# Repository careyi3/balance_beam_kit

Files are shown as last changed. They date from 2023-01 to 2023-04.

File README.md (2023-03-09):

# Balance Beam Kit

Welcome to the source for all of the resources relating to the Ball & Beam kit! This is where we host all of the downloadable resources for the project including the documentation.

To get started with the project, please [head over to the docs site!](https://careyi3.github.io/balance_beam_kit/)

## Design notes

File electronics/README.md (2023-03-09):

# Electronics

Here are all the GERBER files required to produce the PCB for this project along with a BOM and CPL file required to assemble the boards with JLCPCB.

To learn more about the electronics for this project, [head to the electronics section of the docs!](https://careyi3.github.io/balance_beam_kit/electronics/)

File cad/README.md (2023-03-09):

# CAD

Supplied here are the `.stl` files needed to print your own versions of the required parts.

Also included here is my g-code for printing the parts on my Ender3 V2. These g-code files are included for my reference to keep track of my own work, these more than likely won't work for you, do not use them, please slice your own.

To learn more about the mechanical assembly for this project, [head to the assembly section of the docs!](https://careyi3.github.io/balance_beam_kit/assembly/)

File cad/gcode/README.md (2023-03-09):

# G-Code

* DO NOT USE *

This g-code was generated for my Ender3 V2 and has absolutely no guarantee of working for your printer. Please slice the `.stl` files provided under `../meshes`.

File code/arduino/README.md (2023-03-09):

# Code

Included here is test and sample code for the rig. Under `ball_and_beam` you will find the main Arduino sketch implementing a simple PID loop to stabilise the ball along the midpoint of the beam.

Along side the main code under `tests`, you will find simple test code for interfacing with the stepper via the driver and for interfacing with the acoustic position sensor.

To learn more about the code for this project, [head to the programming section of the docs!](https://careyi3.github.io/balance_beam_kit/programming/)

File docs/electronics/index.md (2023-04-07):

---
layout: page
title: Electronics
permalink: /electronics/
---

In this section we are going to break down our discussion into four main topics for discussion; stepper motors and drivers, the Arduino microcontroller, the ultrasonic position sensor and finally the PCB. Before we talk about the PCB I have also included a basic diagram of a breadboard version of the circuit and some tips on assembly etc. The most advanced topic of the discussion is the PCB and in this section we will also discuss the details of the design of the power switching circuit on the board. The final section is optional and fairly abstract, but if you want to dive into some analog electronics design, it's worth a read.

&nbsp;

---

&nbsp;

## Arduino

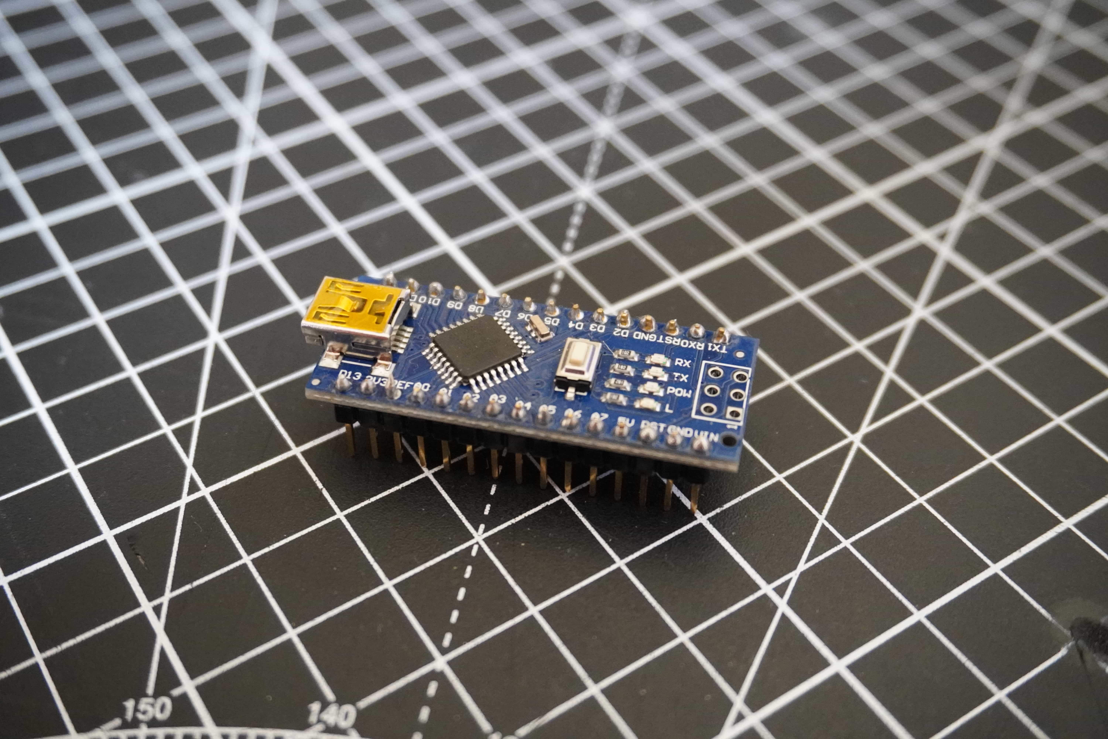
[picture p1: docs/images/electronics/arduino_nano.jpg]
arduino nano


An Arduino is a low cost, flexible, simple and robust microcontroller development platform originally built around Atmel microcontrollers. In the wild, microcontrollers are the smart chips that control electronic devices. Microcontrollers are tiny programmable computers that exist on a single chip. In terms of electronics, they occupy the space somewhere between things that are simple on-off devices with analog components and fully fledged computers. That is to say, a microcontroller can typically interface with simple low level electronics but can bring some intelligence to them while not having the power of a full computer. Even tho these devices don't have the computing power of full computers, modern microcontroller are incredibly powerful and capable of doing amazing things. Microcontroller shine in their ability to do relatively complex tasks at a low level very fast while consuming very little power. Consider that a modern computer has to be able to do lots of different things all at once, typically a microcontroller only has to do one or a small hand full of things at a time; in this way, they can be highly optimised for the task at hand.

While there are loads of different kind of microcontroller available these days, Arduino's provide a great platform to learn embedded software development and electronics. It should be noted that "an Arduino" is a development board and accompanying software stack for developing embedded software projects and not specifically a microcontroller. The microcontroller is the little chip on the board that is the brains of the operation. However, Arduino's are usually referred to as microcontrollers, all be it slightly incorrectly. Arduino's are cheap and very robust, they are hard to blow up compared to other kinds of microcontroller, and when they are blown up, they are easily replaceable. Arduino's also come with a companion software development environment and a whole host of nice libraries and hardware abstractions which means you can get up and running really quickly. There is also a huge online community ready and willing to provide support.

For all of the above reasons and more, I choose to base the kit around an Arduino. I also have a lot of experience personally working with these devices so it was quick for me to prototype the system using one.

To learn more about Arduino I suggest visiting their [website](https://www.arduino.cc/) where you can find loads of information on them. Aside from the basic background presented here, we will dive into more detail about working with an Arduino in the [programming](../programming) section of this guide.

For this project, we will use an Arduino Nano. You can use any Arduino for this, but if you wish to use the PCB for the project, it has a socket which will accept an Arduino Nano. Also note, if you are sourcing an Arduino for the first time, you can buy them from the Arduino website, however these days you can buy many many clones of them online. They are all largely the same, some might have slight differences. Largely these are fine to use but buy them at your own risk as some can be faulty. With that said, they are usually available at a fraction of the price of the branded versions.

&nbsp;

---

&nbsp;

## Stepper Motors & Drivers

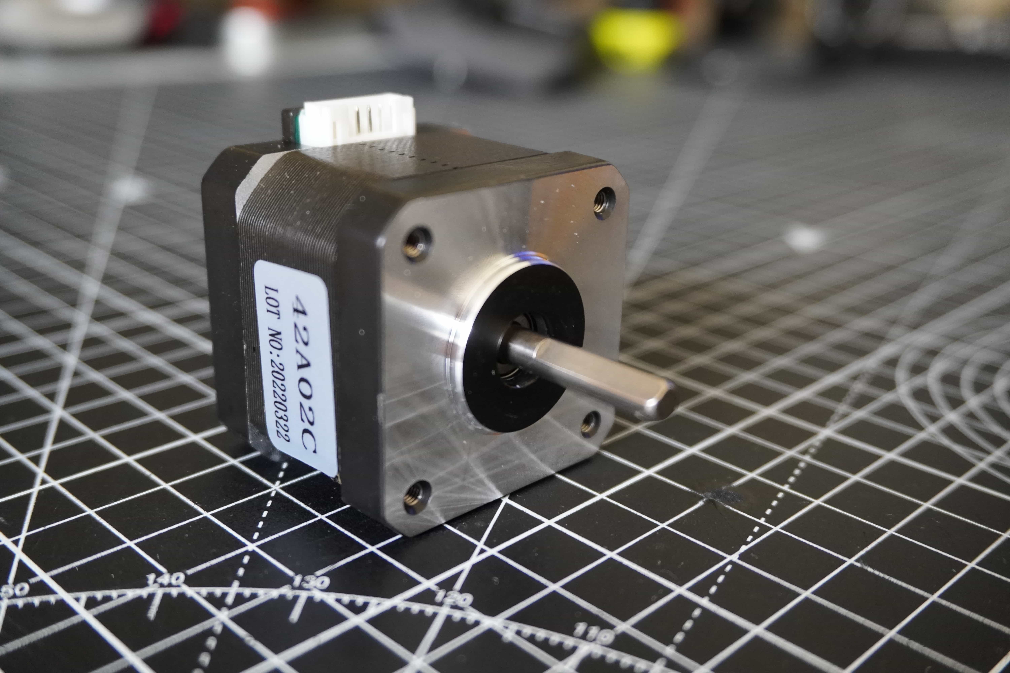
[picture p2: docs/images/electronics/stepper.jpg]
stepper


Stepper motors are a special kind of brushless DC motor that are capable of accurate positioning with no external sensors under normal operation. This means that you can command the motor to spin a certain amount of degrees and hold it's position. The motor will move to the commanded position and stay there with very little error. This effect is achieved pulsing coils in the motor in a certain pattern, the magnetic field created with these coils then interacts with a specially shaped toothed rotor in the motor snapping the motor between so called "steps".

In this way, each rotation of the motor is actually made up of lots of small "steps" hence the motors name. In effect stepper motors are sort of like a poorly designed DC motor in that each state the motor gets into it doesn't really want to leave. This also means that at each step the motor has a very powerful holding torque and doesn't want to slip. These traits can be leveraged in many applications to make stepper motors extremely useful.

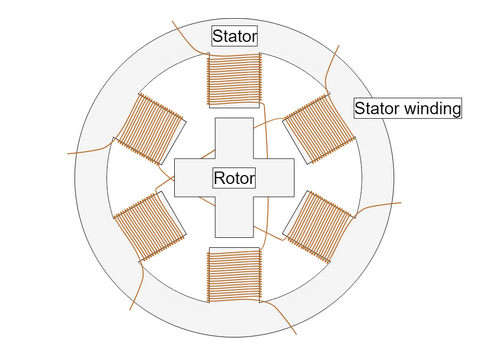
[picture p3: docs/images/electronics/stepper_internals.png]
stepper internals


In terms of machine control, you can work out how many steps correspond to a certain about of movement of an axis of a machine. Once this is known, you can tell the machine how far to move the axis byt sending the correct number of steps to the motor. Due to the way the motors moves in steps and doesn't want to slip from it's holding position, this is extremely accurate and does not require sensors to detect the actual position.

One common modern usage of stepper motors is in low cost desktop 3D printers. The prevalence of these devices has made the NEMA 17 form factor of stepper motor widely mass produced and easily purchased the world over for very low cost. However, they do come with certain disadvantages including extra complicity in their operation. Compared to a regular DC motor, stepper motors require a driver and controller to function. Typically you would use a stepper driver board to interface directly with the motor and a microcontroller to tell the driver when to step the motor. Thanks to the 3D printer market, stepper drivers are also widely available and cheap such as the DRV8825 and in general microcontrollers are also cheap these days, so the expense might not be huge but there is a step up in complicity with compared to flicking a switch for a DC motor.

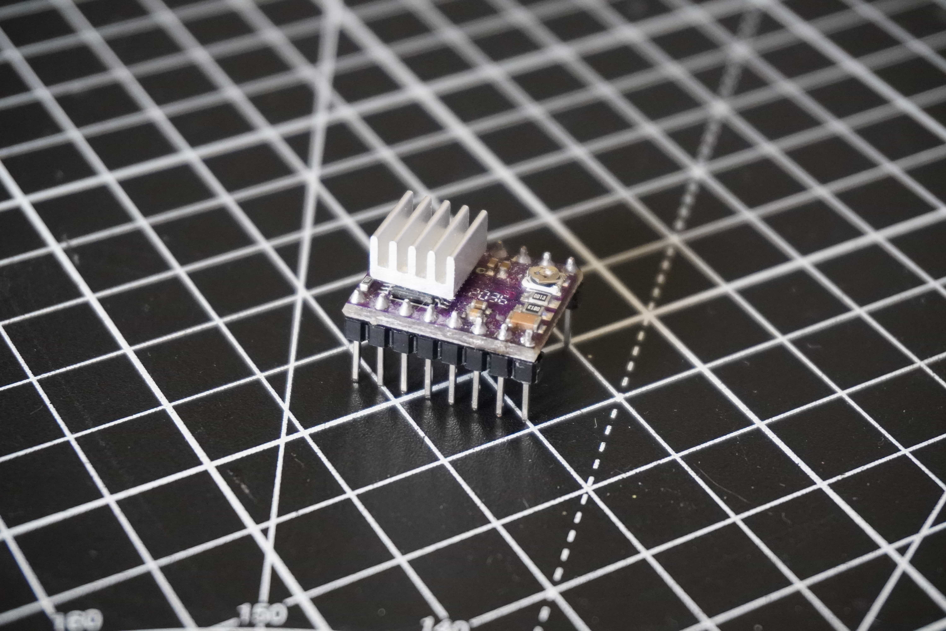
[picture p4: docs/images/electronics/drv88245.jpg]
DRV8825


Considering all of the pros above, a stepper is a decent choice for this project. However it may not be the best choice for all control type projects. The nature of this machine means that the motor doesn't need to move very fast. While moving fast is something stepper motors can do, there are limitations to how fast an Arduino can drive a stepper and so if you require very high speeds this might not be the best solution.

Without going into hugh detail, it's worth knowing that the maximum speed your stepper can attain with be related to how fast your driver can send pulses to the motor (along with how fast your motor can respond to the pulses). The driver in theory will send a pulse to the motor every time it receives a pulse from the microcontroller. Typically the driver will have a "step" pin, by pulsing it high and low from the microcontroller, it will then send a "step" pulse to the motor. There is a minimum pulse width required by the driver and also a theoretical max frequency of the pulses set by the clock speed of your microcontroller. For an Arduino using the widely used [AccelStepper library](https://www.airspayce.com/mikem/arduino/AccelStepper/) this more or less ends up maxing out the pulses per second to 4000 on an Arduino with a 16Mhz clock.

&nbsp;

---

&nbsp;

## Ultrasonic Position Sensors

In our system the "feedback" loop is created by the use of a HC-SR04 ultrasonic position sensor. This is a low cost high performance method of detecting objects by bouncing high frequency sound waves off them and measuring the time of flight of the pulses as they echo back to the module.

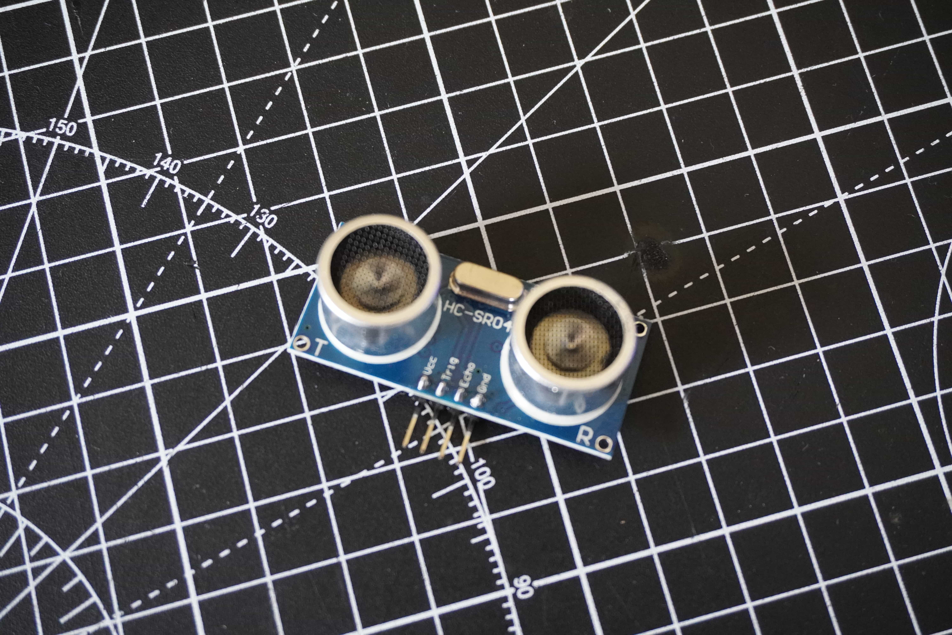
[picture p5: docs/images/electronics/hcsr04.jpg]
hcsr04


If you look at the modules you will see that there are two pieces that look like little speakers. In reality one if a speaker and one is a microphone. When the device is triggered, the speaker side emits pulses of sound which are then reflected back and picked up by the microphone side. The device generates output pulses which can then be measured by a microcontroller to determine the distance of the object reflecting the sound back to the sensor. Below is a graph of what the signals look like as they are transmitted.

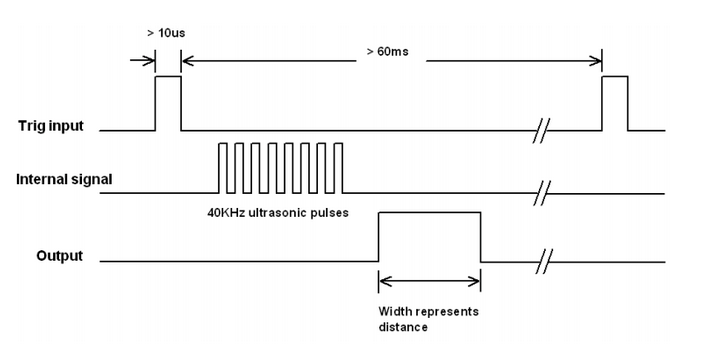
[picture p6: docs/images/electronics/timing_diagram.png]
timing diagram


These modules are fairly accurate however they have some limitations. Due to the nature of their signal, they work best when help perpendicular to a flat smooth surface. They also don't like turbulent air or high frequency vibrations in their vicinity. The only real limitation for our use case is that they also have a small deadzone as you get close to them, but this is handled by the design of the beam which has a built in buffer between the ball and the face of the sensor.

&nbsp;

---

&nbsp;

## Breadboard/Protoboard Circuit

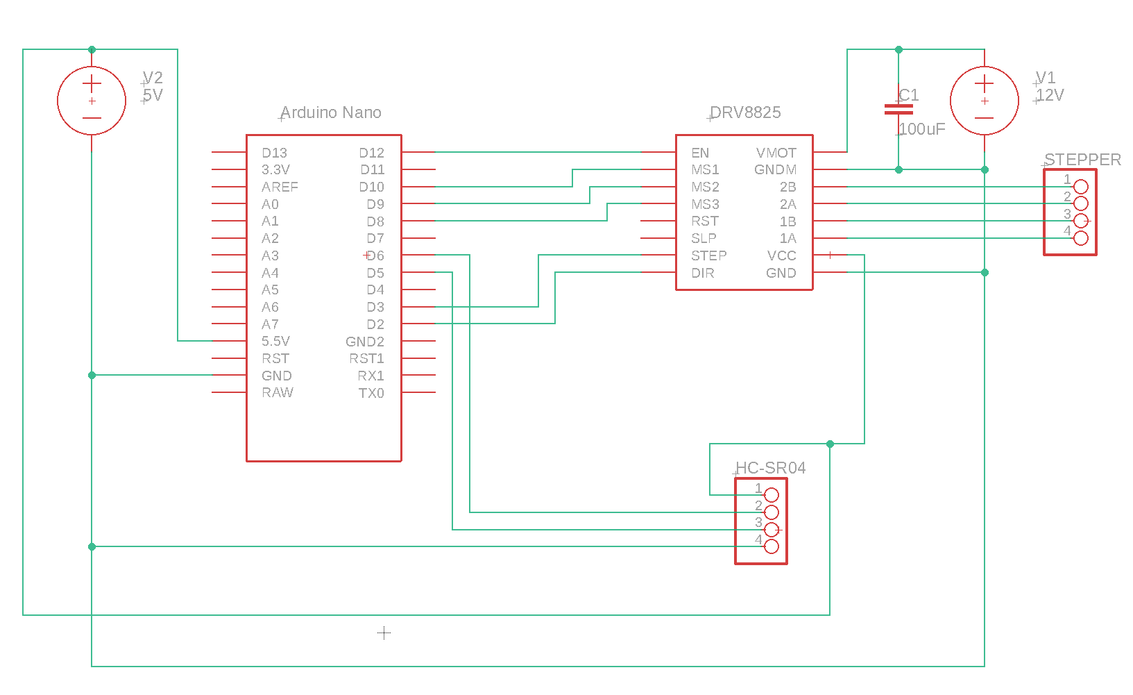
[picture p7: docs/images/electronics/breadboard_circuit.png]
breadboard circuit


The circuit above is fairly simple but there are a few nuances to take into account. Firstly, I would suggest powering the entire thing from a single power supply. I recommend a 12V 2A DC Walworth power supply. This will provide enough current for the motor and also can be stepped down using a voltage divider or a regulator to give 5V for the other electronic. Either this or you can use a USB cable to power the Arduino which will provide the 5V needed for the rest of the circuit. I like to use a single power supply so that I am sure I have the same ground everywhere.

There is a single 100uF capacitor connected to the motor supply line. This is simple an anti ripple capacitor. It is common for cheap power supplies to have some rippled in them, this helps to get rid of this which prevents noise from impacting the driver. This is an important component and it should not be left out.

&nbsp;

---

&nbsp;

## PCB

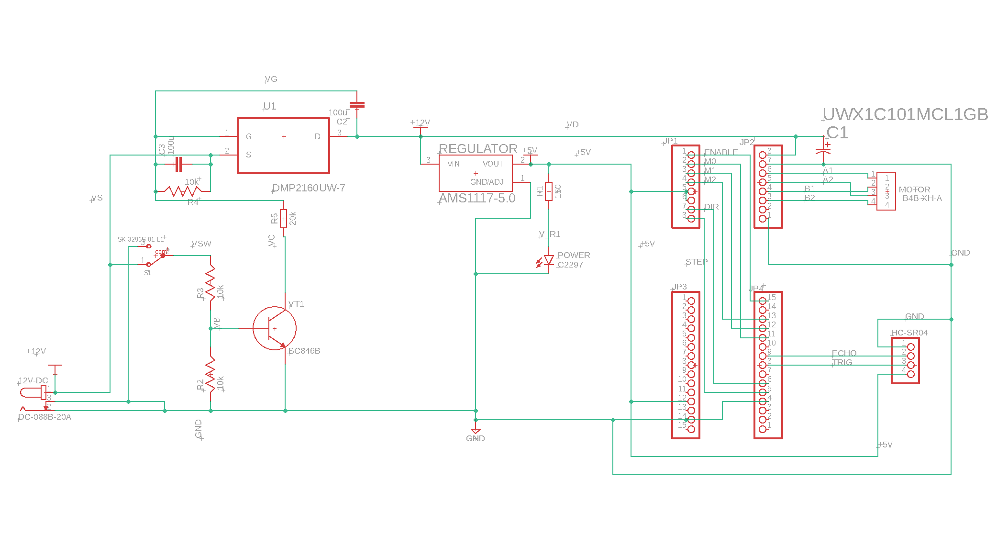
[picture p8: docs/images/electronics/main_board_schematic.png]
circuit diagram


For this project I designed a PCB because it was something I hadn't done before and wanted to try it out. With the consideration that this might one day be part of a kit, it also made sense to do this. If you are building your own version of this, the PCB isn't necessary unless, like me, you want to go through the process of getting one manufactured. That said, the design process is the more valuable part of getting your own made.

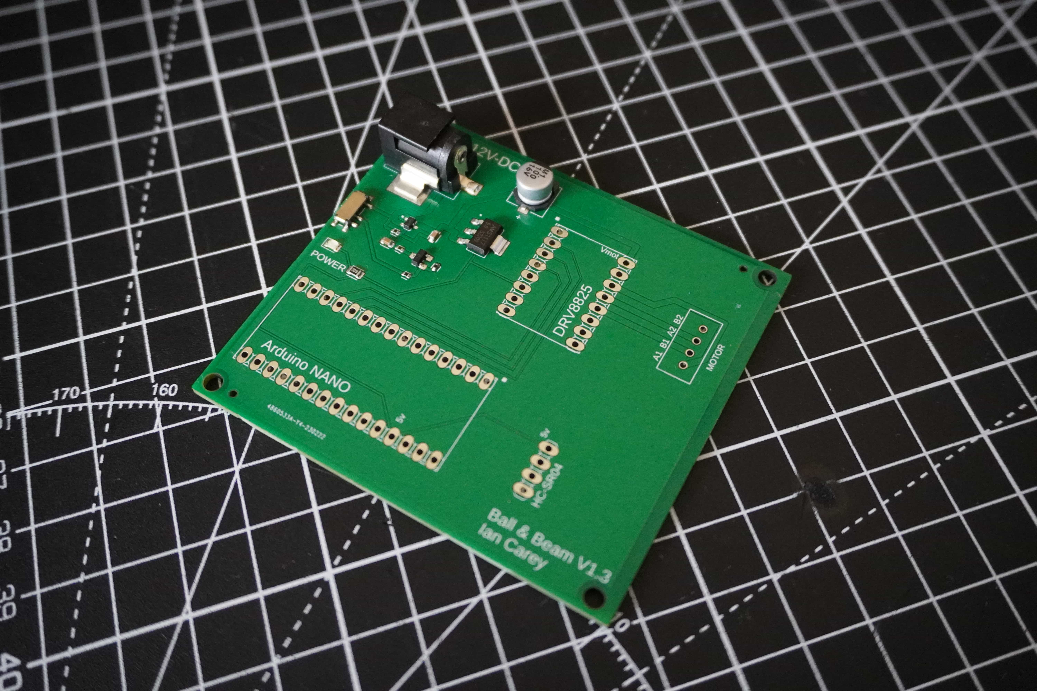
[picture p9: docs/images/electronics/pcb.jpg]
pcb


I'm not really an expert in PCB design and it's not critical for the project, so I am not going to go into much detail here. However, if you want to get your own made, you can find all the GERBER files [here](https://github.com/careyi3/balance_beam_kit/tree/master/electronics/manufacture) along with the bill of materials which will be accepted by the manufacturer I used [JLCPCB](https://jlcpcb.com/).

The PCB is really simple, it's mostly just plumbing together parts to make them nice and neat on one board. The traces are mostly just to connect the Arduino to the DRV8825 and to provide a port to plug the motor and sensor into. The most interesting bit of electronics on the board is actually the power supply that I designed with some help. I will go into this in more detail in the next section. It is however a more complex topic and totally unnecessary for the project. Feel free to skip over the next section unless you are specifically interested.

&nbsp;

---

&nbsp;

### Power Circuit

When I decided to design the PCB for this system, I knew I was getting myself in for lots of things I didn't know and lots of things I had log forgotten from studying engineering years ago. One thing I knew is that the power switch wasn't going to be simple. This might seem strange, but switching can be a tricky thing to do, especially on a PCB with components of varying power consumption. In our case, we have a power switch which needs to cut off power to a microcontroller and a sensor module, no big deal, these devices draw very little current, any tiny pcb mounted slide switch could handle it. However, we also need to cut off power to the motor driver and driver board, this is where the tricky part is. If you think about a basic switch, it's normal closed state is a broken circuit where the supply is on one side and the load on the other, no current flows, all good. When the switch is flicked, suddenly the supply and the load are connected, depending on the load, this could end up drawing a lot of current. Now, in our case the max current we could expect is in or around 1.5A max, that's not a huge amount of current in general, but, when you think that all of it will be being pull through a tiny little switch, you can probably guess the issues that might arise. In fact, if you look at the specs for most of the tiny slide switches on the market, they are all only rated for tiny current. Pulling anything close to 1A through them would surely burn them out immediately.

With all of this in mind, we need to come up with a solution to be able to switch a relatively heavy load on and off, with out the switch itself physically carry any of the load current. There are many ways to do this including the age old and simple mechanical relay. However, a more modern solution to the problem would be to use a switching circuit made up of transistors. Transistors are effectively electronic switches which can be turn on or off by changing certain conditions around them. Typically the physical components have three pins and by wiring them in a certain way, you can make them only conduct across their input and output when a certain voltage is provided to another one of their pins. Now, that is a very basic explantation, their are different flavours of these transistors and the ways in which they work is more complex than I described above, but that's the basics of what you should know about them. In our switching circuit we use two transistors to make our switch work. The full circuit diagram I used to design and simulate this is below. We won't worry about all of the circuit as some of it is just set up to simulate things, but I have highlighted the important parts.

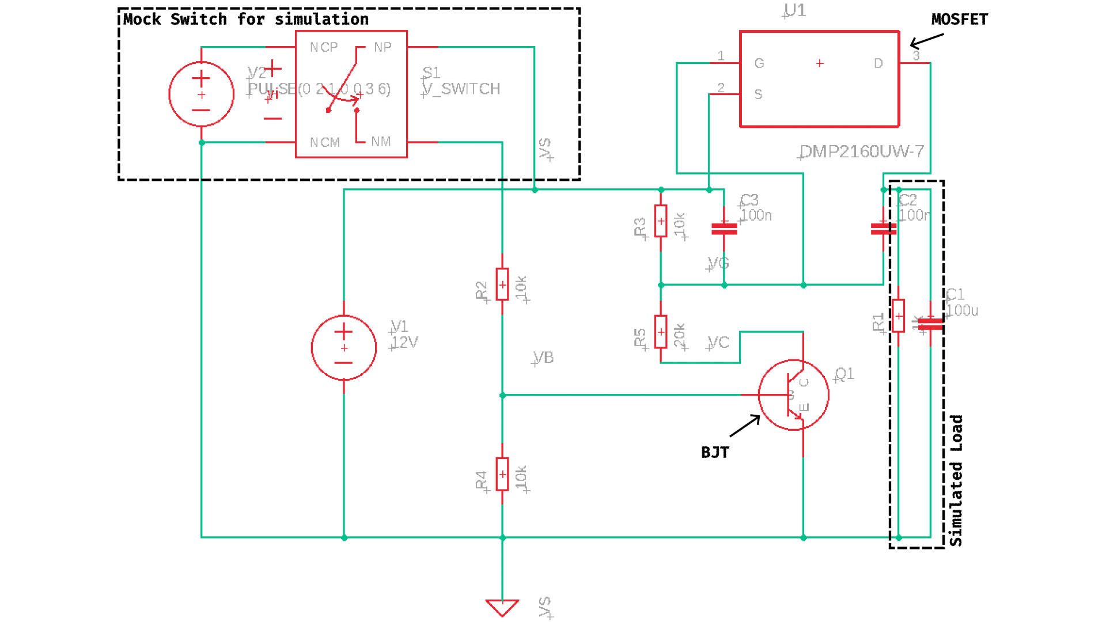
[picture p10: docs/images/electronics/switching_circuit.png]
switching circuit


In our circuit we are using two transistors which have slightly different characteristics. I won't get into the details of their differences but the two types are a Bi-Polar Junction Transistor (BJT) and a Metal-Oxide-Semiconductor Field-Effect Transistor (MOSFET). In terms of naming, I will just say that the pins on a BJT are named the collector, base and emitter. While on a MOSFET they are called the source, gate and drain. You can sort of think of the base and gate pins as being the on/off pins with the other two being the input and output. These components are highlighted in the above diagram. Also highlighted above are the two parts which are just for the simulation. These include an imaginary RC load and a switching circuit which allows for the "switch" to be flicked on and off in the simulation to see the different states over time. In your head, you can replace this with a normal switch being turned on and off by hand. Let get into how the circuit works.

In the initial state, the switch is turned off. With the switch off, the base of the BJT is pulled to ground via the resistor R4, this in effect turns off the BJT and no current flows between the collector and emitter. If we now look at the MOSFET, we see that it's gate pin is connected to a voltage divider in line with the collector of the BJT. With the BJT turned off, the lower branch of the voltage divider is ignored and with no current actually flowing through the gate of the MOSFET (that's just how they work), the voltage at the gate is effectively 12V i.e. it matches the supply voltage. You will notice that the source pin is also connected to the same 12V and so their is no voltage different between them. This is important, because the MOSFET will only turn on when the voltage difference between the source and gate exceeds a certain amount. Now, lets talk about the case when the switch is turned on. With the switch turned on, the BJT now has it's base connected to some proportion of the supply voltage. In this specific set up the BJT will enter "saturation" and will conduct between the collector and the emitter. Now if we go back to the voltage divider connected to our gate, the end of the divider at R5 is now effectively connected to ground meaning that the voltage divider now acts as normal and the voltage at the gate of the MOSFET will be 8V thanks to the 1:2 ration of the resistors R3:R5. We now have a case where our gate is at 8V and our source is at 12V. Now, the threshold of voltage difference has been exceeded and the MOSFET will turn on and conduct between source and drain. In our case, the output of the drain powers everything on our board.

The above is dense and I have glossed over many parts but I hope it makes some sense as to how we can switch a high load circuit without the switch it's self actually carrying any of the current. The only component in this circuit that really carries any current is the MOSFET. It just so happens that MOSFETS are designed very well for this task. The relatively high resistor values in the rest of the circuit are specifically to limit current flow in the switching circuit. The BJT is also not dealing with any high current either. As a final note, I haven't spoken about the two capacitors on the source and drain of the MOSFET. These are called charging capacitors and help lower the current spikes when the switch is turned on. If you have a load with lots of capacitors on it, when you turn on the power, all of the capacitors will effectively charge up all at once. This can cause a massive spike is current draw on switching and can lead to components blowing as they aren't rated to handle this. These charging capacitors help to smooth out the sudden current draw caused when switching a capacitive load.

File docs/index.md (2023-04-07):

---
# Feel free to add content and custom Front Matter to this file.
# To modify the layout, see https://jekyllrb.com/docs/themes/#overriding-theme-defaults

title: Welcome!
layout: home
---

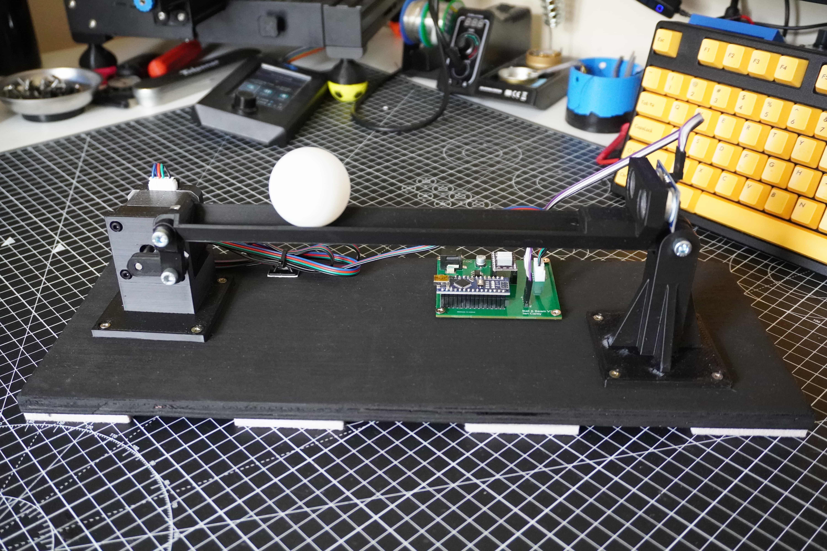
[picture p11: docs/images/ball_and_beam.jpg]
ball and beam


This is main project site for the Ball & Beam kit by Ian Carey. This guide covers everything you need to know to get up and running with the Ball & Beam kit from assembly, to programming to the theory behind how it works! The below sections are laid out so that they build on each other but you should jump in and out of them in what ever order makes the most sense to you.

All of the source materials, code, 3D printing files can be found here on the projects [Github repo](https://github.com/careyi3/balance_beam_kit). Enjoy!

The development of this kit has been fully documented on the creators YouTube channel, if you are interested, you can find the entire build series [here](https://www.youtube.com/playlist?list=PLMqshdJjWZdnB4wa5L2HWYxcJ6pagYxFq).

&nbsp;

---

&nbsp;

## Bill of Materials (BOM)

This is a list of all the materials you will need for this project. This project is currently still a fully DIY kit where we are only supplying the guide but you must supply all the parts. In future we hope to release purchasable kits that will contain the parts. For now, this is the best we can do.

[BOM](./bom)

&nbsp;

---

&nbsp;

## Assembly

Instructions, with photos, of the mechanical assembly of the rig. The assembly is straight forward enough involving only 5 3D printed parts all of which should easily be printable on most common 3D printers. For reference, all of the parts for this were designed to be printed on an Ender 3 V2.

[Assembly](./assembly)

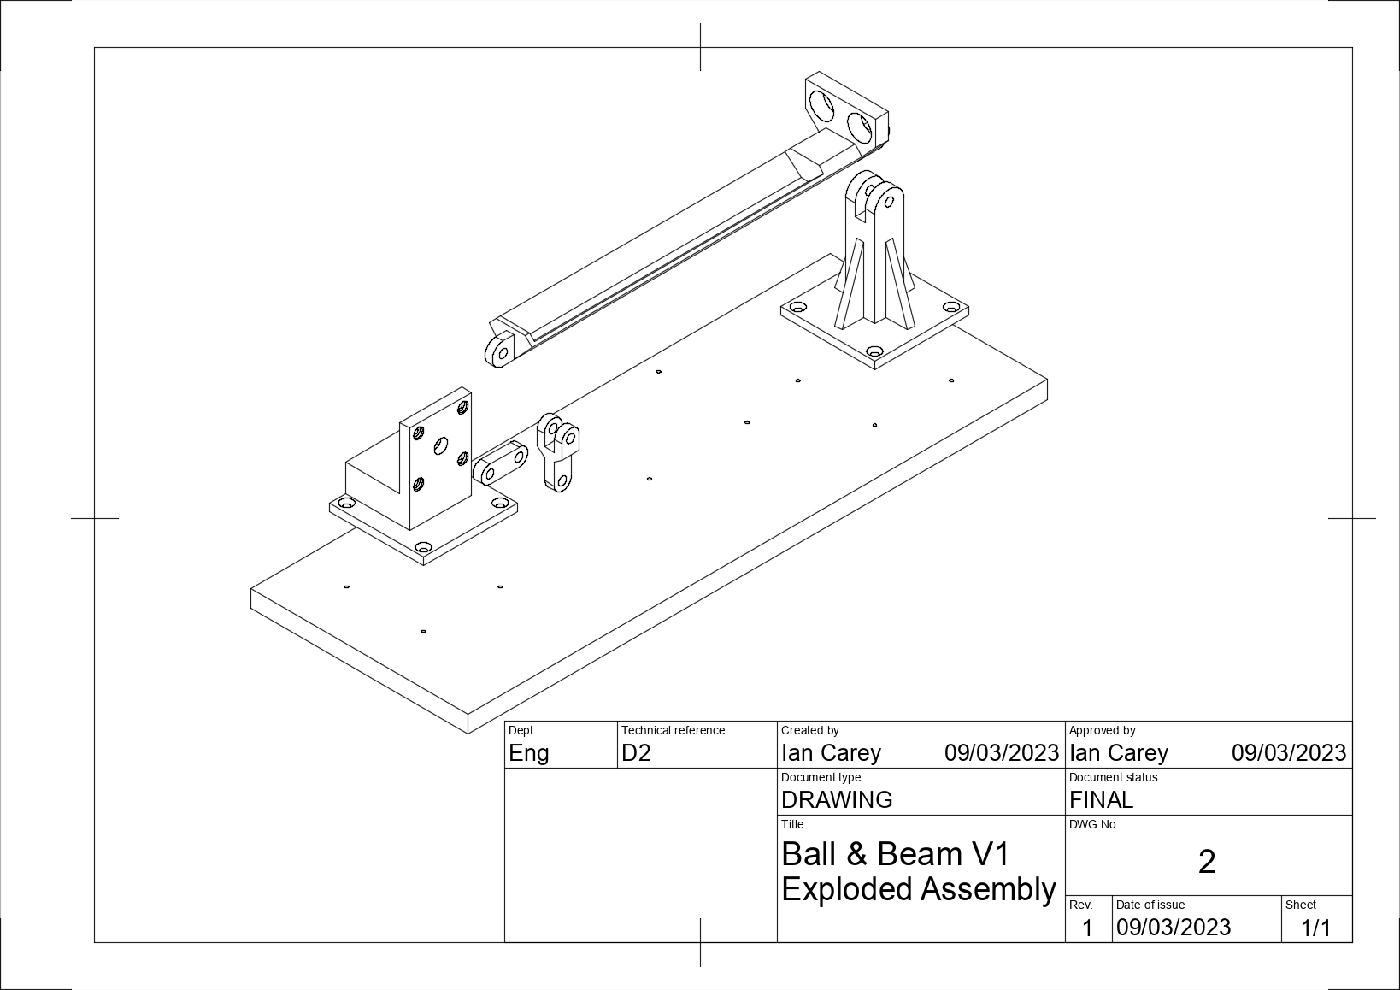
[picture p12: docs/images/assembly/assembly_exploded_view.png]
assembly_exploded_view


&nbsp;

---

&nbsp;

## Electronics

Details all of the the electronics involved, Arduino, stepper motors, position sensors and details of the PCB design.

[Electronics](./electronics)

main board schematic

&nbsp;

---

&nbsp;

## Programming

Details of the code involved in the system and working with the Arduino platform. We will also dig into the various libraries used in the project and how they work.

[Programming](./programming)

&nbsp;

---

&nbsp;

## Control Theory

In this section we will do an overview of the concepts behind control theory. The goal is to use as little maths as possible to give good overview of how a PID controller works and how it applies to our problem.

[Control Theory](./control_theory)

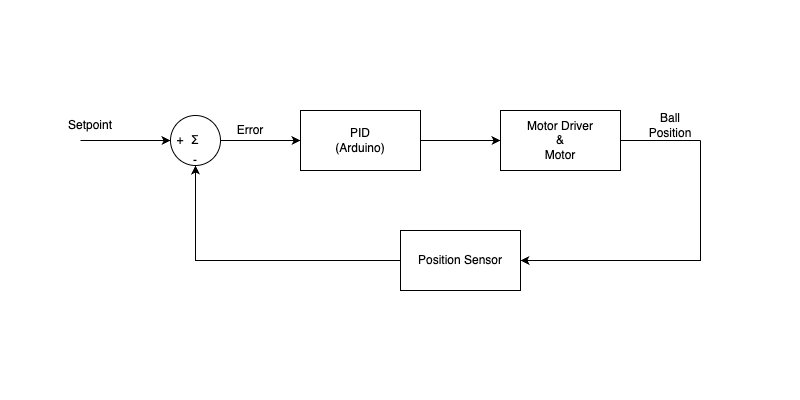
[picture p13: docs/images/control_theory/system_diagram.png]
system diagram


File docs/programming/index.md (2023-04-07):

---
layout: page
title: Programming
permalink: /programming/
---

In this section we will provide a basic overview of getting started with programming an Arduino microcontroller. We will then jump into some more complex discussion of how some of the important parts of the code work under the hood.

The sample code provided for the system is [here](https://github.com/careyi3/balance_beam_kit/blob/master/code/arduino/ball_and_beam/ball_and_beam.ino).

I have a [video on YouTube](https://www.youtube.com/watch?v=OBsXWNbOTRY) breaking down the code and going over it in some detail, it is a good companion to this guide if you want to take a look.

&nbsp;

---

&nbsp;

## The Basics

The Arduino platform is an extremely powerful and easy to use platform for getting up and running with embedded software development projects and requires very little prior knowledge to get started. The basic flow of how the system work goes like this; your microcontroller (usually an Atmel chip for Arduino) is soldered onto the Arduino board, you connect your Arduino board to your computer via USB. Using Arduino's software tools, you write your code in C/C++. Once written, the Arduino software interfaces with the microcontroller on the board and uploads your code to it. Once powered up, the microcontroller on the Arduino board then executes your code continuously. This flow is a little different to how production grade chips would usually work. Typically, microcontrollers require a special programmer to program or flash them with the required machine code. With Arduino, this is avoided by the microcontroller coming with a "bootloader" pre installed. This bootloader allows a very high level software interface to program the chip over USB.

I am not going to go into the details of setting up your first project with an Arduino, there are countless resources online for this the best of which is the basic Arduino getting started guide. If this is your first time working with this platform I highly recommend you take a look and follow the [getting started guide](https://docs.arduino.cc/learn/starting-guide/getting-started-arduino).

The rest of this section is going to go into the details and usage of specific libraries used in the example code for the system. It assumes that you have the code downloaded and can follow along with it. You can grab the code [here](https://github.com/careyi3/balance_beam_kit/blob/master/code/arduino/ball_and_beam/ball_and_beam.ino).

&nbsp;

---

&nbsp;

## AccelStepper Library

Stepper motors, as we covered in the electronics section, require more than just a simple on/off switch to control. Along with the stepper driver board, you need to write some code on your microcontroller to tell the motor driver when to send pulses. At it's most basic, you can interface with a stepper driver by pulsing a pin high and low (high for a minimum duration of 10us usually) at a particular frequency. On an Arduino, you can do this using `digitalWrite` and `delay`. This isn't the most advanced way of doing it, but it will work. Of course, the speed them of the motor is effectively controlled by the frequency of the pulses. So sending a step high low pulse with a shorter `delay` value between each pulse, you can make the motor spin faster.

While the above mechanism for pulsing a motor will work file for lots of different cases, it lacks some features that are very important for controlling a motor. One major thing missing from the above is acceleration. When working with electric motors in general you will find that one way they are specced is with torque-speed curves. These are plots of the amount of torque they have a certain speeds. A rough way to think about this is that the motor will have less torque at higher speed. So if you had a machine, like a cnc machine with a large enough mass, you can't just tell the motors to go full speed from a dead stop. The motors will stall immediately the not be able to move the machine. Instead you can start the motors spinning at a slower rate and ramp the speed up to full speed. A ramp down can then be used to slow the machine down to stop precisely at the desired location. These so called acceleration profiles are a bit more complicated to implement so it might be nice to use a library that implements this for us.

For this project I used the [AccelStepper](http://www.airspayce.com/mikem/arduino/AccelStepper/) library which handles basic operations of a motor as well as implementing accelerations and different operating modes like running a motor at a specific speed or moving it a specific number of steps at a certain speed. Thanks to stepper motors precise open loop position control, the software can also provide accurate tracking information on the exact angle of the stepper motor, including how many revolutions it's moved through and in which direction. I have used this library in many projects and I can honestly say I think it's fantastic. I strongly recommend having a read of the documentation and getting to grips with how it works, it is highly worth while. It has lots of config that is worth understanding including the limits to the maximum speeds and accelerations.

&nbsp;

---

&nbsp;

## HC-SR04 Library

With reference to the electronics section where we presented the timing diagram for this device, we should remember that the width of the pulse returned by the device should be measured to determine the distance from the sensor and object is. To trigger the device, all we have to do is send a pulse of a certain length to the device on the trigger pin. We then need to "listen" for a response on the echo pin and record the length of it. This might sound complicated but we can achieve the trigger pulse by using `analogWrite` and `delay` and we can listen to and record the response pulse length using the `pulseln` function. There is then a tiny bit of maths that needs to be done involving the speed of sound to turn the pulse length into a distance. None of this is very difficult bu there is a nice library we are using here which wraps all of this up in a handy package. You can find the source code [here](https://github.com/gamegine/HCSR04-ultrasonic-sensor-lib/). I recommend having a read of it and understanding what is going on.

&nbsp;

---

&nbsp;

## Kalman Filter

The above sensor library and the sensor module are pretty good at what they do especially considering the price of the modules. They have their limitations but within their operating ranges they work pretty well and should achieve enough accuracy for most hobby applications. The range of the sensors is from about 2-400cm, so if you are detecting objects at around a meter or so away and you don't need to worry about variances of 1-2cm, these sensors will work perfectly as they are. In our application, we are using the sensor in about the 2-30cm range and within that range a 1-2cm variance is going to be way to much error for the PID controller to stabilise it properly. Now, in real life, over the 2-30cm range the sensor isn't giving 1-2cm of variance, but there is still some noise in the sensor readings making them a little harder to use in the PID controller. As the PID controller changes it's input based on the error signal from the sensor, if this error signal has lots of noise, the PID controller has to compensate for this making it difficult to reach stability.

We can improve the situation a lot by using something to smooth out the noise in our sensor readings. There are many different ways to achieve this but by far one of the most effective ways is to use a Kalman filter. I am not going to go into the details of a Kalman filter here as they are a relatively complex and deep topic. For an amazing coverage of them, I highly recommend following [this tutorial on YouTube](https://www.youtube.com/playlist?list=PLX2gX-ftPVXU3oUFNATxGXY90AULiqnWT), watching the first 4-5 videos in the series will give you a really good working knowledge of the basic version used in our project here (I have always struggled with these and this videos series really cleared up lots for me). At a very high level view, the Kalman filter uses predictions of errors compared with actual measurements of values to build a model of the system under the hood. Amazingly, this model very quickly approaches an extremely accurate output of the real values of the system even if there is lots of noise present.

Regardless of if we understand the details or not, we can ignore the implementation if we use one of the great Kalman filter libraries available to us! For this project we use the excellent [SimpleKalmanFilter](https://github.com/denyssene/SimpleKalmanFilter) library as it works well for a single variable and doesn't over complicate the system. I suggest reading their docs about setting up the library but really we are only required to pass in some tuning parameters to initalise the state of the filter. These can also be tuned with trial and error to get it working the way you want.

&nbsp;

---

&nbsp;

## Coding a PID Controller

The main logic of the code for the system essentially follows a pattern of; read sensor -> process data -> command motors. This continues in a loop forever attempting to balance the ball at a set point. The part in the middle, "process data", is where the magic really happens in converting the sensor data into the correct motor commands to make the machine do what it needs to do. In specific it does this by implementing a PID controller. In the next section of this guide I will dive into control theory and the basic intuition around how a PID controller works and what it is doing. In terms of the software, we are using a library in the example code, but coding your own PID controller isn't very hard once you understand the concept. If you already know a bit about this subject but haven't seen how to do it from scratch I recommend you take a look at this [YouTube video](https://youtu.be/RZW1PsfgVEI) that walks through a basic from scratch implementation of a PID controller on an Arduino. If you don't know anything about PID controllers I recommend going to the [control theory](./control_theory) section and reading up and coming back to this video later.

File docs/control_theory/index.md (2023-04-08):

---
layout: page
title: Control Theory
permalink: /control_theory/
---

The main goal of the project is to act as a resource for teaching the basics of control theory and in particular the practical implementation of a PID controller. Below is a system diagram showing the main components of the system and their connection in the common system diagram format.

system diagram

Before we dive into the details, there are two videos of mine which will help, this first one is dedicated to explaining the [software behind the system in general](https://www.youtube.com/watch?v=OBsXWNbOTRY) and the next one is an in depth look at [implementing your own PID controller from scratch on an Arduino](https://youtu.be/RZW1PsfgVEI) (you may want to wait until after you have read this to watch, or not, who knows!).

## What is a System?

In engineering there came a point where machines started to evolve from being purely mechanical. With the advent of electricity and electric motors, there became a need to use a common framework to control system containing both electrical and mechanical elements. However, before we could control such a system, we need a common way of modelling it. To this end, the idea of systems & control theory started to come about. There are lots of formal maths that surround this topic, however we are only going to lightly touch on that here.

Typically we can thing of a system as being anything either electrical or mechanical or both, that takes some input that we can model and produces some output that we can also model. Usually the model of a system would be some mathematical function where we write the output as a function of the input. With expressions for the input and output we can define something called the transfer function for the system. This is basically a single mathematical expression that defines the characteristic of the system we are working with. Again, not getting into the details but this function is labelled `G(s)` and is the Leplace transform of the input expression divided by the Leplace transform of the output expression. If you feel comfortable looking into the maths behind this, I suggest researching the topic on your own. I can highly recommend Modern Control System by Dorf & Bishop for this topic.

For this discussion I only want you to be aware that a highly complex system can be broken down into a single function that defines it's behaviours and in control engineer we would refer to it via it's transfer function. In terms of control theory, we often refer to the system being controlled as the "plant". We would also often present it in block diagram for like below.

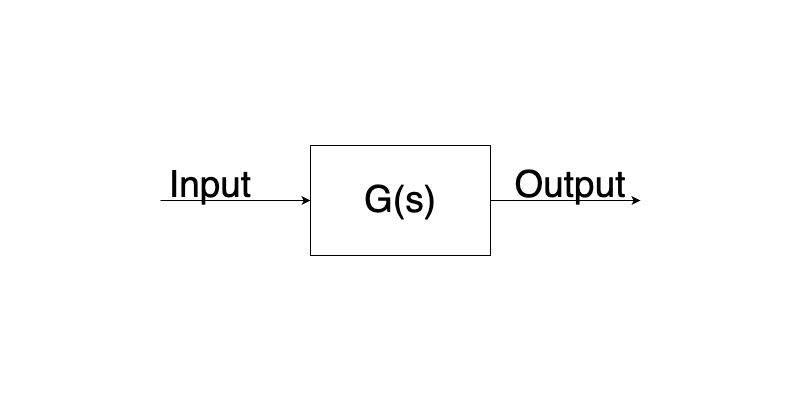
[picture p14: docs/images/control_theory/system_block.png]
system block


The above just simply represents some input to the system, being fed into the system and providing an output. It should be noted that transfer functions can be simple or complex and they can be nested. However, no matter how complex, they can always be boiled down to a single block in a control diagram. It should also be noted that you don't necessarily need to derive the transfer function for a complex system to control it. It is possible to use maths to analytically come up with the best control scheme for a system, but there are other methods, this will become clear later.

&nbsp;

---

&nbsp;

## What is Control Theory?

Considering the above diagram, we have what we would call an open loop system. This means that the input and outputs are totally independent. We feed some input to the plant, it does something, we get and output, but the system doesn't "know" anything about the out or the state surrounding the plant. A good example of a system that behaves like this is our stepper motor. The stepper doesn't know anything about it's state, we just give it an input and it goes to it's output. Due to the engineering of stepper motors we can trust that for the most part this system can be controlled in open loop. Let's consider another real world example of where open loop control might fall down. Consider a cruise control system in a car, we are on a straight flat road travelling at 100km/h. We trigger the cruise control and the system now holds the throttle (the input) at it's current level. This results in the car continuing to travel at the same speed (the output) of 100km/h. Now, lets consider what will happen when we approach a hill in the road. At the point, gravity will act against the car requiring the car to accelerate to compensate for gravity pushing it back down the hill. However, remember, our input doesn't know anything about our output. So the car will begin to slow down and the throttle position won't change at all.

The above example is missing something, we call it feedback. What the cruise control system was missing was the information that the the car has slowed down below the target speed and based on how much it had slowed, it needed to know that it should increase it's throttle to maintain speed. In control theory we would call this type of system a closed loop control system, other terms used are a feedback control loop or simply feedback loop. In these loops we usually have a set point (the desired speed of the car), and output (actual speed of the car), some form of sensor to provide feedback (the cars speedometer) and an error signal (the difference between the desired and actual speed). It should be noted that in these closed loop systems, the input to the plant becomes the error signal from the summation block in the diagram below.

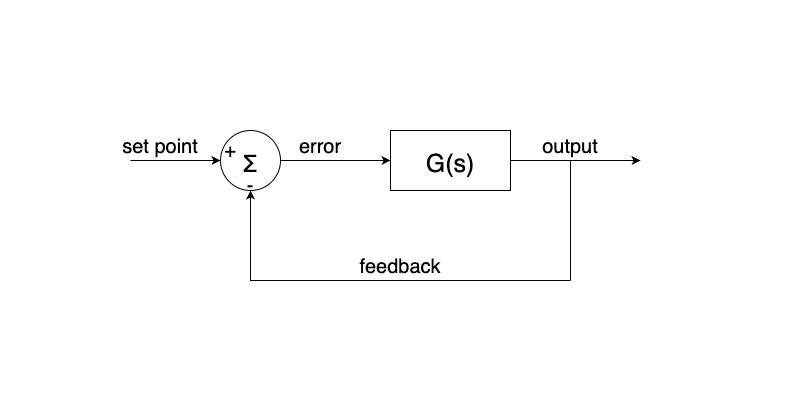
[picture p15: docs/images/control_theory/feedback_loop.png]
feedback loop


Now that we have some working model of how a feedback system works we are in a far better state that we were with the open loop case. However, we are still missing a key ingredient to make the system do what we want. We are assuming that by piping the output of the system back to the input and feeding the error back into the system that we will get the response we desire. This is a fairly large assumption and for the majority of cases this will not work. There are some system that just so happen to be naturally stable and will respond fine to this situation, but that is not the general rule. Most sufficiently complex electromechanical systems are not going to be independently stable. The last missing piece from our system is something called compensation. There are many different types of compensators but one of the most widely used ones, the PID controller, is where we will focus our attention in the next section. To add compensation to a system, we need to insert something between the error signal and the input of the system. What this will do is figure out what the best input should be to the plant to minimise the error signal as much as possible. With some clever maths, these compensators can drastically change the characteristics of a plant and are extremely powerful. So much so that the basics of these system has remained unchanged for 100 years (that's right you don't need computers for these, you can build fully analog compensators...wild!).

Before we move on, as a final note, have a look at the plot below. It is a common type of system response plot that you might see. This should help give some intuition as to how our system will respond when we are trying to get it to settle to some set point. We will start at some value, in this case 0, we will command the system to reach a value, in this case a little less than 1.5. As the system runs, it will begin below the set point with a large error value. This error value will be fed into the plant demanding a large response. The system will respond and end up overshooting the target by a decent margin. At this point the error will turn negative because we have overshot the target and now we need to bring it back down again, so we will change the input of the plant to compensate. This continues for a time until as we see we settle down to a steady state with little or no error. This type of second order system response is really common all over engineering and you will see it in some many different systems. Have you ever noticed in a home heating system how when you change the temperature it sometimes ends up going higher or lower than you wanted first before settling down to the value you wanted? That is because it is doing the exact same thing as I talked about above (and is probably use a PID controller to do it too!).

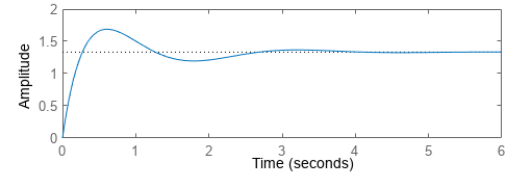
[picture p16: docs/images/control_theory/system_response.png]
system response


&nbsp;

---

&nbsp;

## How Does a PID Controller Work?

The first thing we should do is present a diagram of what a PID controller looks like that we can refer back to. The below is more or less the same as before, but we have have the PID block added. I have exposed it's internals to make it clear how the parts interact, but again, we would usually just leave it as a single block in a system diagram.

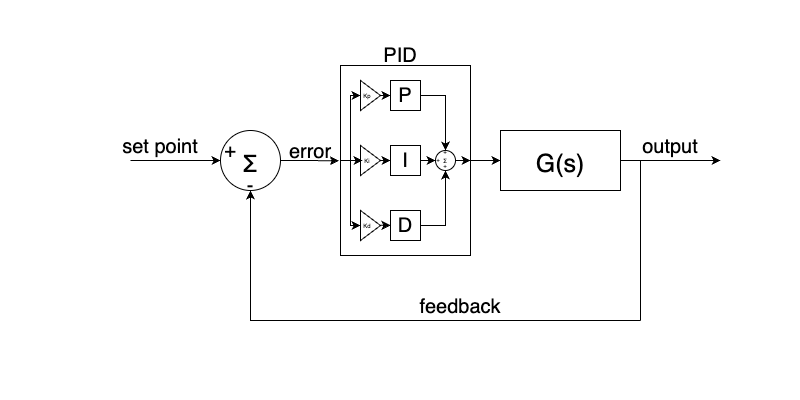
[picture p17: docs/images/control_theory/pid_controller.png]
pid controller


The above might look a bit confusing but we can break it down into little chunks and explain each part. Firstly, lets talk about the name of this type of controller P.I.D. This is an acronym for Proportional, Integral and Derivative. What the block diagram is showing is how these terms combine to produce the input to the plant. Each part of the PID controller receives the error signal. There are then gains applied to the signal for each part. I haven't spoken about gains before, but you can think of them as being just constant numbers you multipliy the error by in order to scale it. Overall, their effect is to determine how much of an effect on the overall result each part of the controller has. We use the letter `K` to denote a gain, so in our case the three gains are `Kp`, `Ki` and `Kd`. So imagine I want the proportional part of the controller to be weighted twice as much as the integral, I could set `Kp = 2` and `Ki = 1`. If For example I didn't wan't any derivative parts in the controller, I could set `Kd = 0` and that would remove it's influence completely. Moving on, the error signal is used by each part, scaled by the gain to produce some output for each part. These parts are then all added back together to produce the input for the plant. The way in which we actually control the system is by choosing values for `Kp`, `Ki` and `Kd`. Remember earlier when I said you can use maths to figure out how the controller should be set up to achieve your desired results? Well, this is what I meant, you can derive ideal values for these parameters and plug them in. However, this is not the only way to do it!

Up until now I haven't told you what each part of the PID controller is actually doing. If you build up some knowledge of what these parts do and how they interact, you can roughly tune a PID controller with no maths at all and just an intuition for how the system will respond. This is where this topic starts to feel more like art than science and for sure tuning PID controller is a skill that you need to develop over time. Outside of the hobby realm, even if you use tools to derive the equations and computers to spit out the ideal PID values, they will usually be based on approximations made by the model for the system which are usually simplified. They might get you 90% of the way there, but the rest is often down to trial and error and tuning the values by hand.

Let's start our discussion about the parts starting with the `P` term. This is the simplest term of the three. As the name would suggest, this term just provides a response that is proportionally based on the error signal. It does this simply by multiplying the error signal by the `Kp` gain. This effectively is just going to scale the error in some way either making it larger or smaller. Often times scaling the `P` gain alone is enough to make a system stable but often it is not. One intuition for this is that it can cause the system to respond faster or more aggressively the larger the gain is. This means that for a small error signal you could get a very large response which might be desirable in some cases, but in others it might throw off the stability massively.

The `I` term is where things will start to get a little more complex. `I` stands for integral in the mathematical sense of the word. We aren't going to go into detail here, but essentially integration seeks to find the area under a certain curve. In the abstract, if you have a signal the varies over time, the sum of that signal at each point over time is effectively the integral of it. So for the controller, the `I` keeps track of all of the past error values and continually adds them up with respect to the time that has passed. This might seem strange, but think about a system where something is oscillating back and forth around the set point. There is a constantly changing error signal moving plus and minus the whole time. The `I` term will sum these errors and it's effect will increase in the overall output which can help to reduce the steady state error.

Finally let's talk about the `D` term. Again, as before, `D` starts for the mathematical concept of a derivative. Without going into it too deeply, you can think of a derivative as the rate at which something is changing. So in our system, if a value changes suddenly, the `D` term can end up being very large in response to this. This can be useful if you need a system that responds quickly to sudden changes in state, but it can also cause high frequency noise and is very sensitive to instability. It can in fact be so difficult to tune that often it's gain is set to zero leaving only the `P` and `I` terms. This type of controller is called a `PI` controller. Where it is left in, it typically has a fairly small gain value to prevent it dominating the other two terms creating instability.

That's about it for the basics of control theory. I suggest that you go and watch the following two video if you haven't already. After reading, they may make a bit more sense if you ahd previously tried to watch them! Here they are again, the [software behind the system in general](https://www.youtube.com/watch?v=OBsXWNbOTRY) and an in depth look at [implementing your own PID controller from scratch on an Arduino](https://youtu.be/RZW1PsfgVEI).

If you have made it this far and have read everything in order, congratulations! You are now finished all of the supporting materials for this kit. I hope they have been helpful and I hope you feel ready to tackle the kit and have fun playing with it!

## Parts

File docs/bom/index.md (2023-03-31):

---
layout: page
title: BOM
permalink: /bom/
---

The below parts list is more or less everything you need to get working on this project. Due to the DIY nature of the kit, the list is not exhaustive specifically in relation to the electronics. If you are building this on a breadboard or proto-board you may need more parts that I have listed below. However, the below does contain all of the main parts needed for the project.

| Part | Quantity | Notes |
| --- | --- | --- |
| 400x150mm 12mm Plywood | 1 | This is for the base, any relatively heavy sheet material at least 12mm thick will do fine. |
| 3D Printed Parts Set | 1 | 3D Printing files found [here](https://github.com/careyi3/balance_beam_kit/tree/master/cad/meshes). |
| Nema 17 Bi-Polar Stepper Motor | 1 | Almost any stepper motor available for 3D Printers should work file for this. The electrical characteristics are not critical, however, the motor should have a 5mm shaft with a flat spot. |
| HC-SR04 Ultrasonic Sensor | 1 | |
| Regulation Table Tennis Ball | 1 | Or any light ball of 40mm in diameter (heavier ball will change how the system responds). |
| PCB | 1 | The PCB is optional, the source for it is [here](https://github.com/careyi3/balance_beam_kit/tree/master/electronics) so you can get your own made if you like. Otherwise you can make your own with proto-board from the schematic or assemble it on a breadboard. |
| Arduino Nano Compatible MCU | 1 | Any Arduino should work for this, however the PCB has a socket for a Nano. |
| DRV8825 Stepper Driver | 1 | |
| 22uF Capacitor | 1 | |
| 12V 2A DC Power Supply | 1 | If using the PCB, ensure that you have a 2x6.4mm centre positive barrel jack. |
| 4 Wire Female to Female JST Cable | 1 | This is for the motor. |
| 4 Wire Female to Female DuPont Connector Cable | 1 | This is for the sensor. |
| M3x10mm Socket Head Screws | 4 | Motor mounting hardware. |
| M4x10mm Wood Screws | 12 | Mounting screws for PCB and base pieces. |
| M5x25mm Socket Head Screws | 2 | Linkage mounting screws. |
| M5x20mm Socket Head Screws | 1 | Linkage mounting screws. |
| M5 Nuts | 6 | Linkage mounting nuts. |

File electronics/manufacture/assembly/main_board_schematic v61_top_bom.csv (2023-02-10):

Comment | Designator | Footprint | LCSC Part #
10k | R2 R3 R4 | 0402WGF2002TCE | C60490
20k | R5 | 0402WGF2002TCE | C25765
100u | C2 C3 | 0603B104K500NT | C30926
150 | R1 | RESC2012X65 | C17471
AMS1117-5.0 | REGULATOR | SOT229P700X180-4N | C347223
BC846B | VT1 | SOT-23 | C181138
C2297 | POWER | LEDC2012X110N | C2297
DC-088B-20A | 12V-DC | DC-088B-20A | C145921
DMP2160UW-7 | U1 | SOT65P205X100-3N
SK-3296S-01-L1 | S1 | SK-3296S-01-L1 | C319020
UWX1C101MCL1GB | C1 | PCAP_6.3X5.4-ELECT | C111600

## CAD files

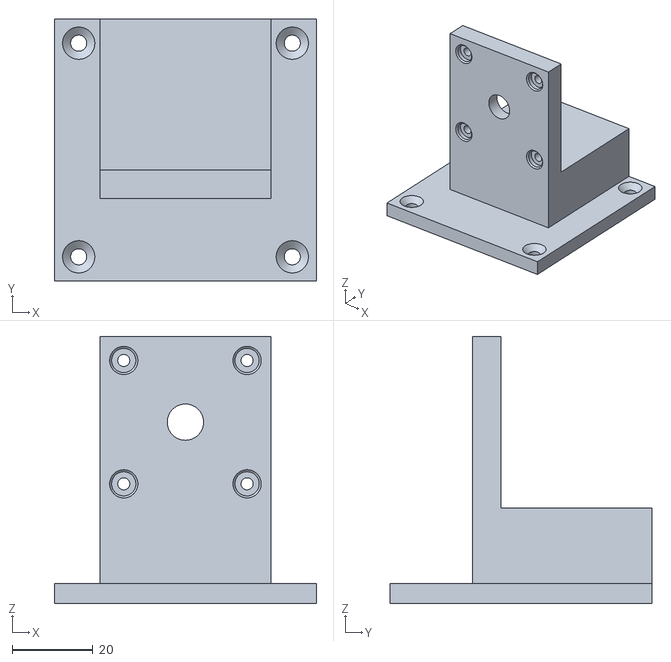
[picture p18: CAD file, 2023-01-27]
cad/meshes/motor_mount.stl
65.0 x 65.0 x 66.2

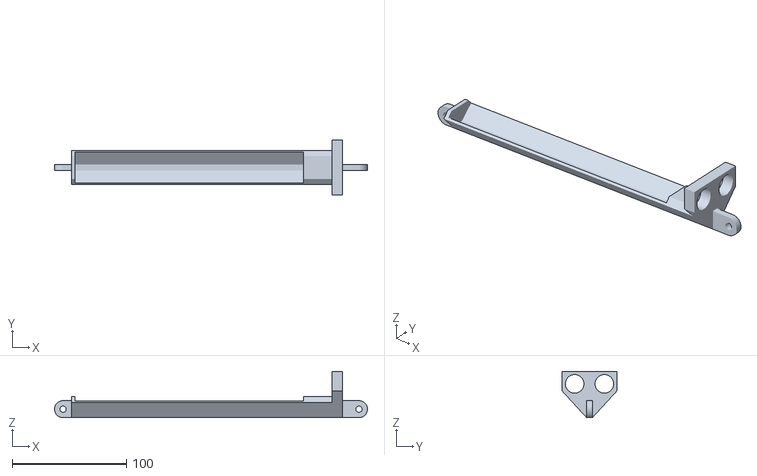
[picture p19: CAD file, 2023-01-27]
cad/meshes/beam.stl
274.0 x 48.0 x 40.7

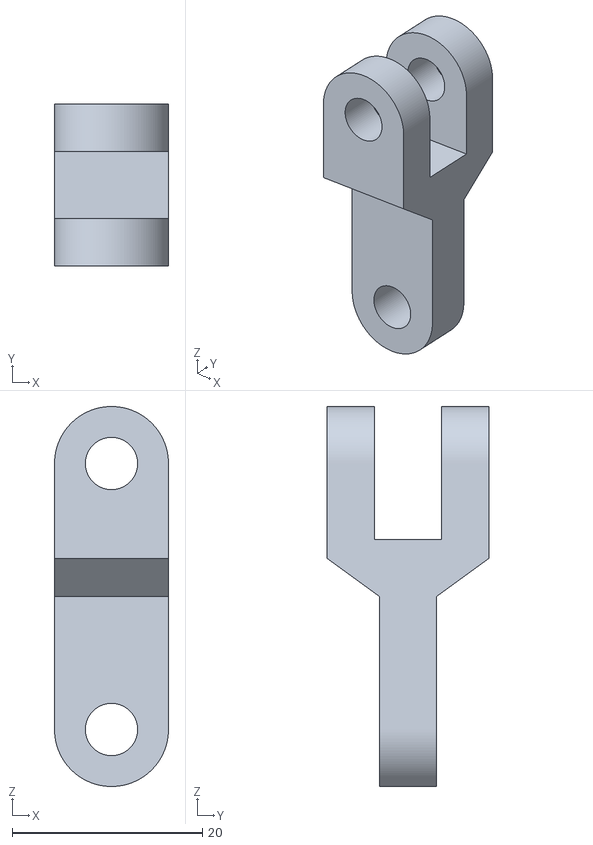
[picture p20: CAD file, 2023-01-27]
cad/meshes/upper_linkage.stl
12.0 x 17.0 x 40.0

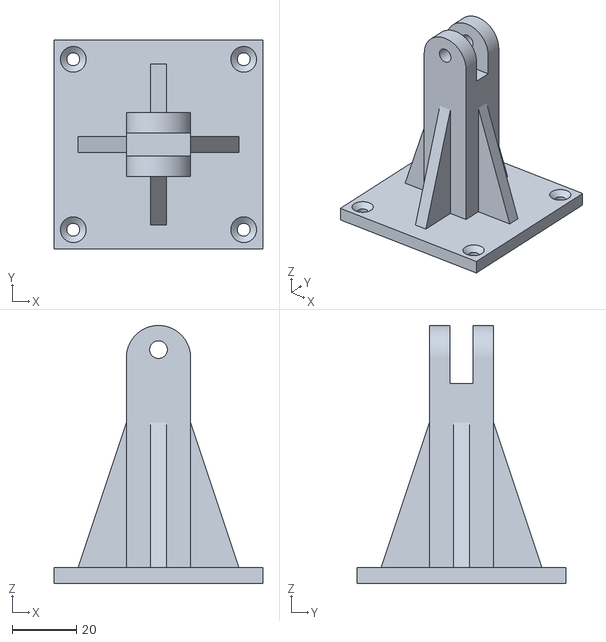
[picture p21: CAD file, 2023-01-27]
cad/meshes/fulcrum.stl
65.0 x 65.0 x 80.2

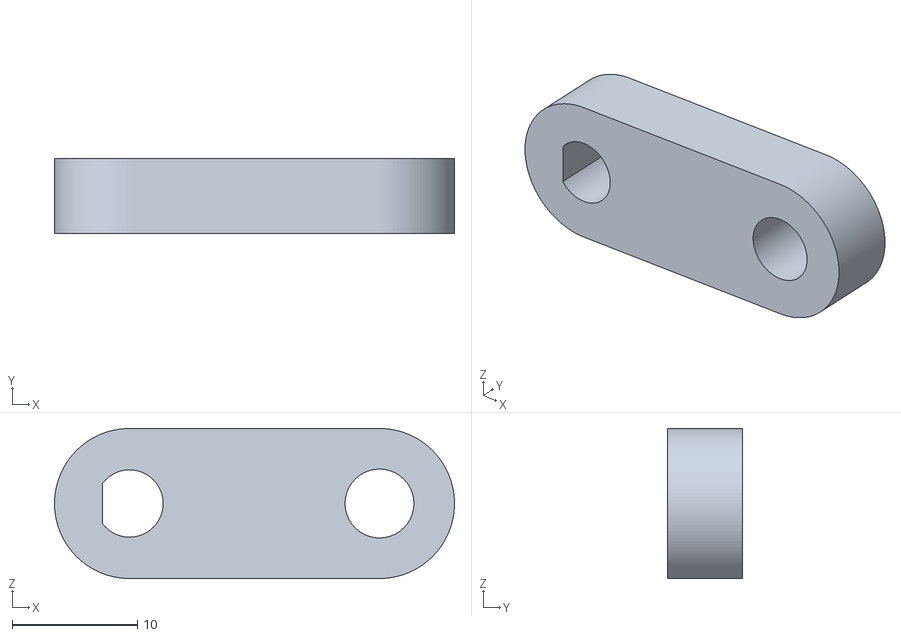
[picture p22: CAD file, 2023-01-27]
cad/meshes/lower_linkage.stl
32.0 x 6.00 x 12.0

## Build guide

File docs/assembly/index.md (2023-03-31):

---
layout: page
title: Assembly
permalink: /assembly/
---

These are the detailed assembly instructions for the Ball & Beam kit with pictures! This guide assumes you have successfully 3d printed the parts and also have a suitable piece of base material to mount everything to. If you haven't 3D printed your parts yet, [here is a link to the STL files](https://github.com/careyi3/balance_beam_kit/tree/master/cad/meshes). We recommend printing in simple PLA, but any material will do fine.

Due to possible tolerance issues with 3D printing in general, the fit of the moving parts below is designed to be loose. We recommend getting a set of assorted small nylon washers to insert into the joints to help pad them out if they are too loose. Equally, we recommend having a small file on hand to make adjustments as needed.

It should also ne noted that this assembly involves a few different lengths of M5 screws. For simplicity these also act as the bearing surfaces for the moving parts. This means that they can come loose over time as the machine moves. You might need to use locking nuts and/or washers to help the parts move more freely and not come loose.

assembly_exploded_view

&nbsp;

---

&nbsp;

## Step 1

The first step will be to prepare your base material to mount the other components to. We recommend a 12mm thick (or thicker) piece of ply wood for this task. The material isn't very important but the only real requirements are that is it flat enough and rigid enough to mount the components to. If it is slightly heavy that is also ideal as it will help reduce vibrations in the rig. The material should also be thick enough to securely accept mounting screws for the 3d printed parts. In our version, we use 10x3mm countersunk wood screws.

To prepare your piece of material, cut it to be approximately 400x150mm. Depending on your material, you might want to give the edges some light finishing with sandpaper to clean off any splinters or burrs. At this point, the base is more or less done. If you have chosen to use wood for your base, you can at this point mount your pieces approximately and screw them down. However, we recommand a couple of extra steps to result in a better finished product.

### Step 1.a

To ensure your rig is properly aligned, we recommend pre-drilling guide holes in the base for your mounting screws. The below hole pattern is more or less the optimal layout for the rig and ensures all the joints will be aligned properly. You can also make your own hole pattern by laying out the pieces by eye and marking the hole positions. Once your holes are drilled we also recommand giving it a coat of paint if it's wood to clean up the finish a bit (we LOVE matt black!).

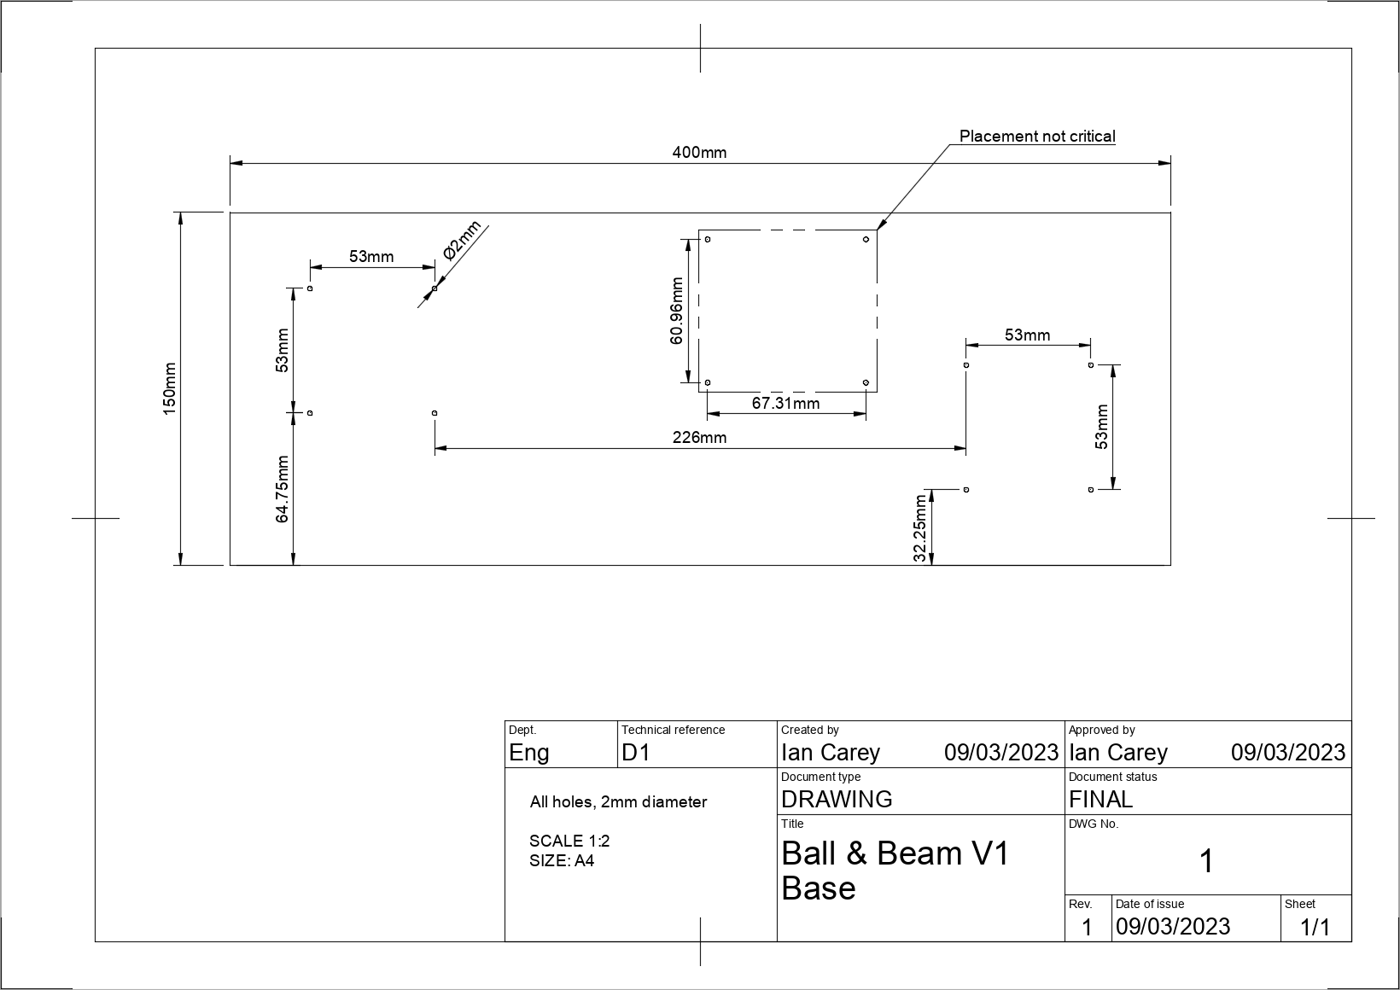
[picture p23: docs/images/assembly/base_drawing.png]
base_piece_hole_pattern


Finally, we recommand attaching either adhesive carpet or rubber pads to the bottom of the board. This can help even out the surface if the base piece has any warp in it and also helps reduce vibrations caused by the machine while operating.

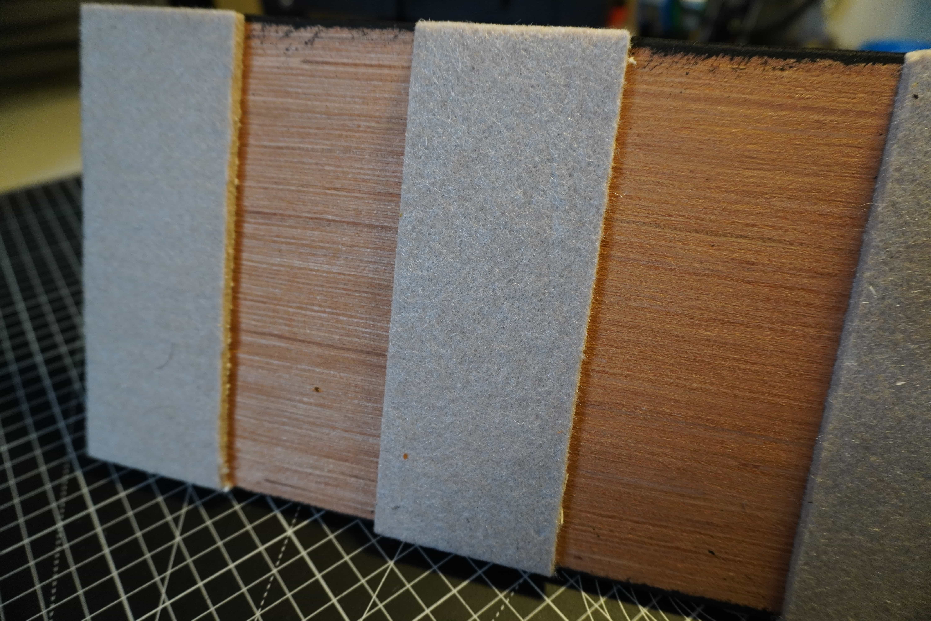
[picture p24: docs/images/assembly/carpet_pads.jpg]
base_piece_carpet_pads


&nbsp;

---

&nbsp;

## Step 2

With the holes drilled, begin to mount your motor mount and fulcrum to the base piece using some 10mm countersunk M4 wood screws. Looking at the front face, mount the motor mount to the left and the fulcrum to the right as indicated in the exploded diagram above. Ensure not to over tighten the screws as the 3D printed parts can easily break if tightened too much.

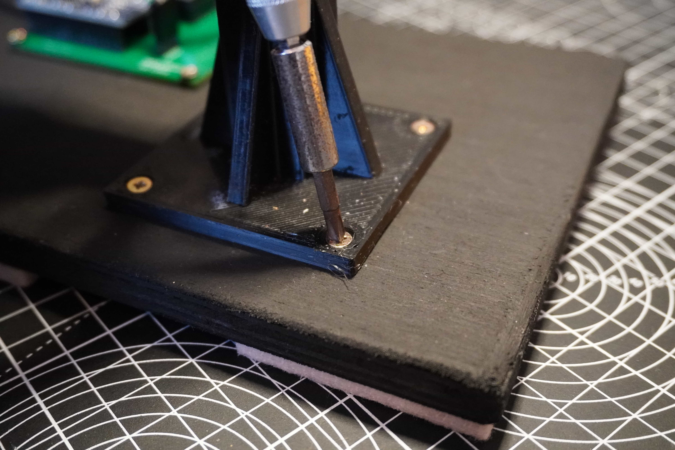
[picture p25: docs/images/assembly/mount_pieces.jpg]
mount_pieces


If you have the PCB for the kit, mount this now using the same screws.

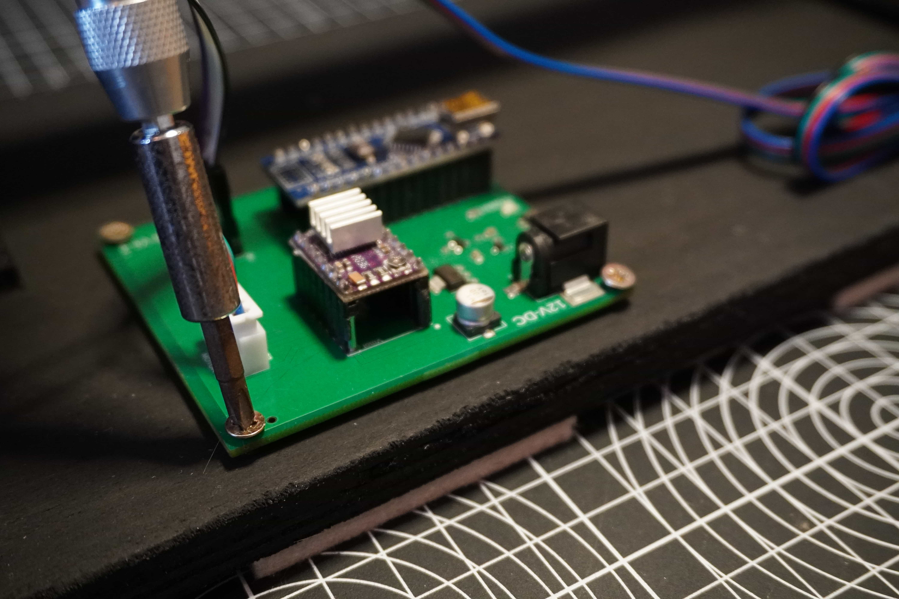
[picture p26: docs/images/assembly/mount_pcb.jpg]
mount_pcb


&nbsp;

---

&nbsp;

## Step 3

Mount the motor by inserting it into the mount from the back. There is a slight recess in the mount which the motor should form a firm press fit with.

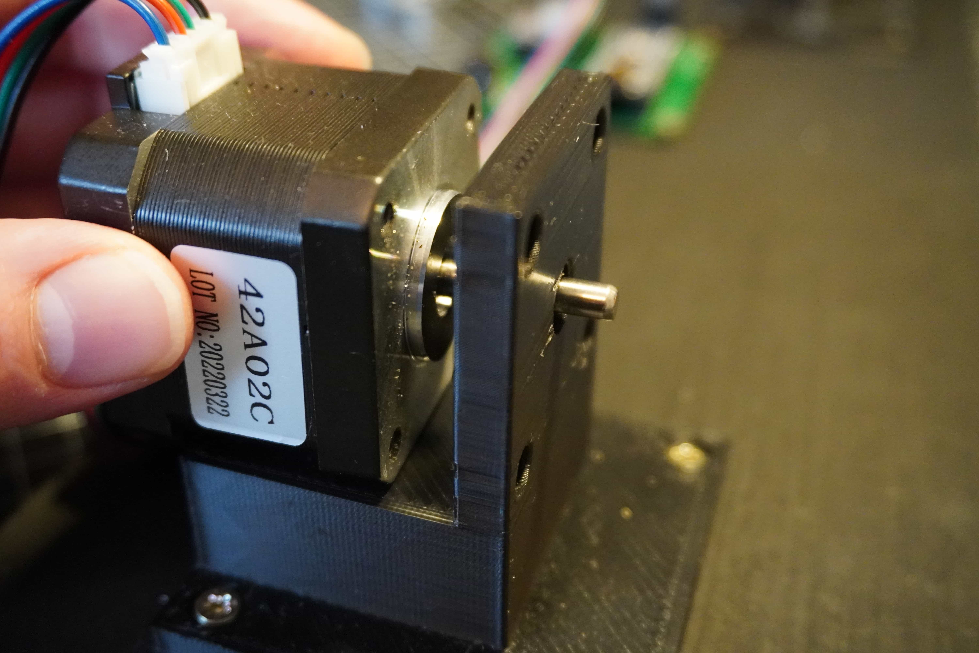
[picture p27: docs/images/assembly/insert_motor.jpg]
insert_motor


Next, fix the motor in place with 4x10mm M3 socket head cap screws. Ensure to start each screw the tighten them incrementally so that the motor evenly pulls into the slot on the mount. Make sure not to over tighten as this might deform and/or break the mount.

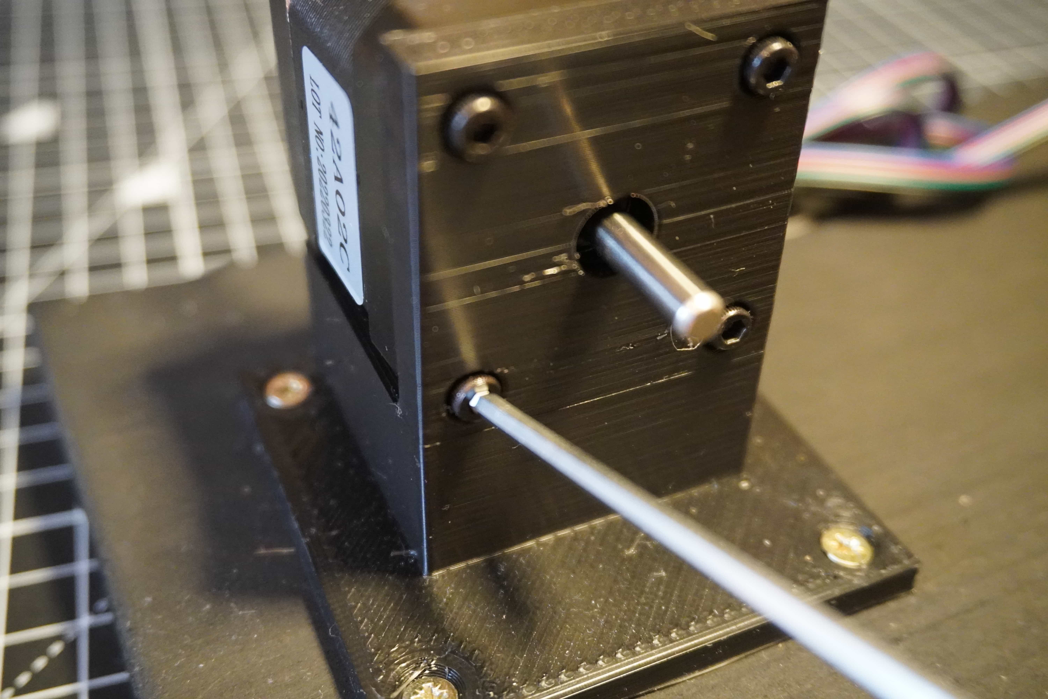
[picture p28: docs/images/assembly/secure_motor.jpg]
secure_motor


&nbsp;

---

&nbsp;

## Step 4

Take the lower arm piece and holding it up to the motor shaft, align the flat spot on the mounting hole with the flat slot on the motor shaft.

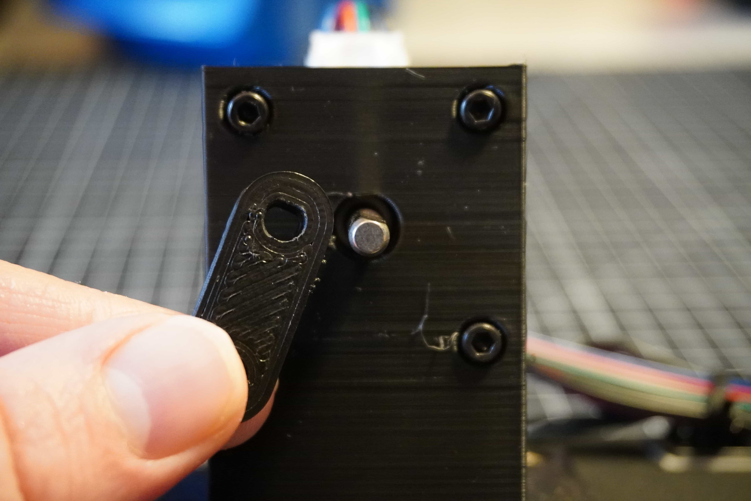
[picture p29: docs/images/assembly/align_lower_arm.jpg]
align_lower_arm


Once lined up, press the arm onto the motor shaft. It should be a tight press fit. If it's too tight, you may need to deburr your parts or use a small file to widen the hole.

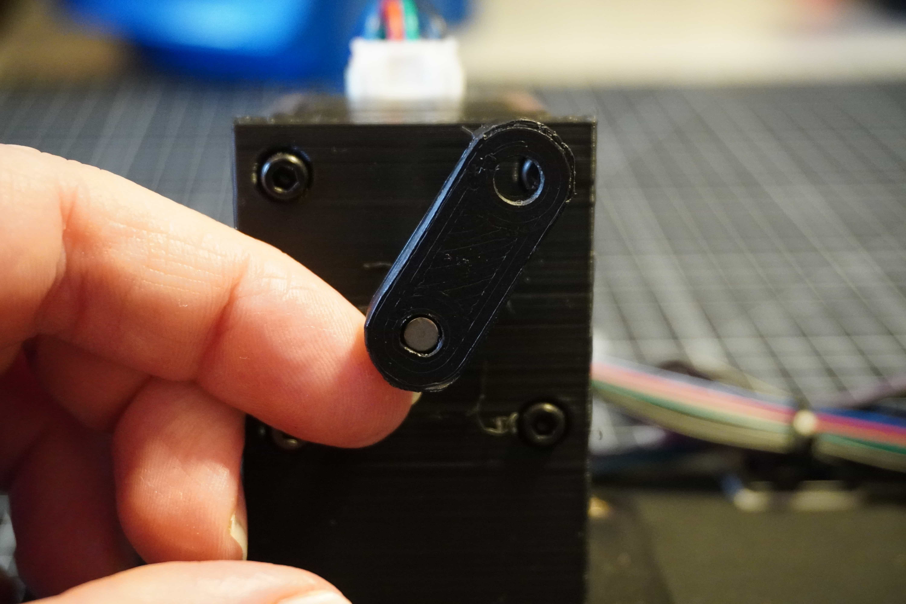
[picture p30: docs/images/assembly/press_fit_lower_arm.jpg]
press_fit_lower_arm


&nbsp;

---

&nbsp;

### Step 5

Once the lower arm is attached, take the upper arm and line it up with the other hole in the upper arm. Ensuring the open end of the clevis (U-shaped part) is facing upwards.

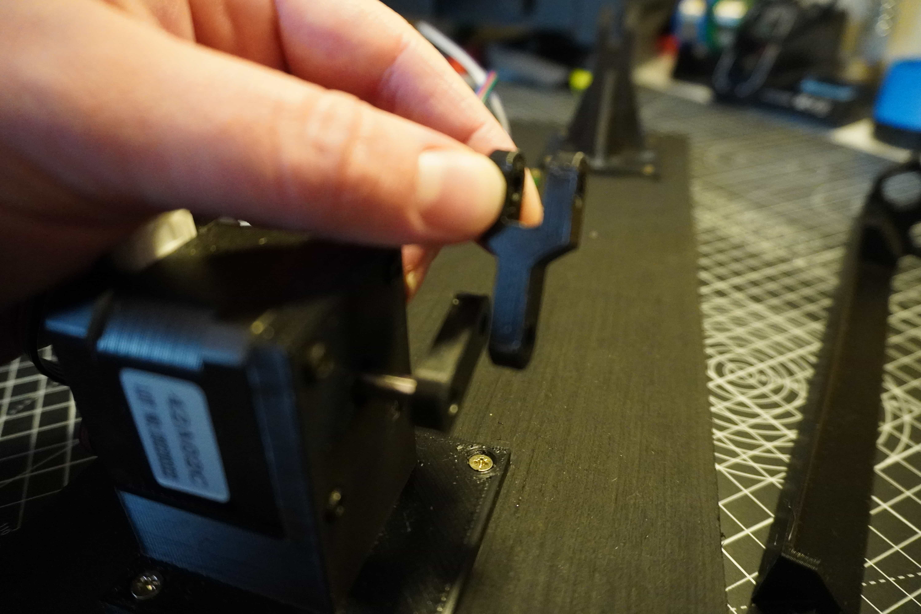
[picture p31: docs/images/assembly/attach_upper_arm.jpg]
attach_upper_arm


Secure the lower and upper arms using an 20mm M5 bolt and nut.

&nbsp;

---

&nbsp;

## Step 6

Insert the end of the beam with the sensor mounting point closest to the fulcrum. Lining up the hole in the beam with the cross-hole in the fulcrum's clevis, insert a 25mm M5 bolt and secure with a nut.

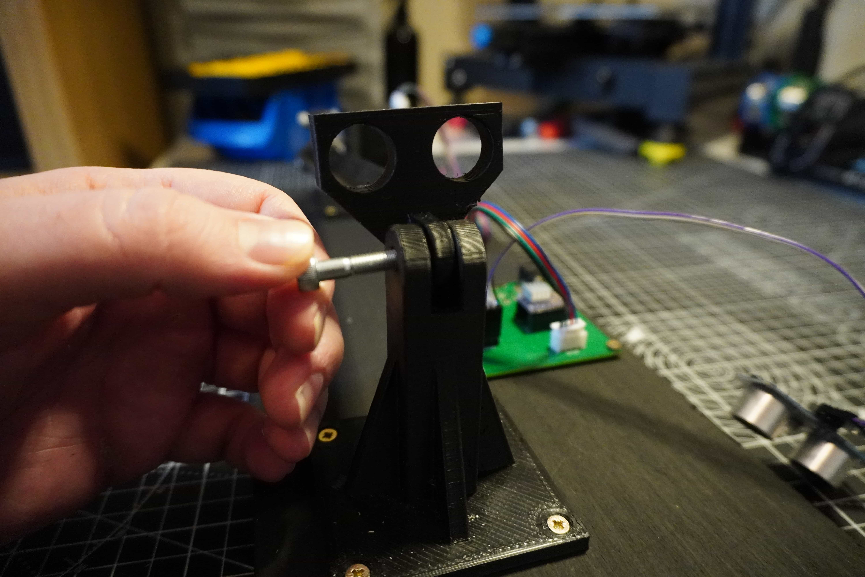
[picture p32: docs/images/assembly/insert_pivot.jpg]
insert_pivot


On the far end of the beam, insert the tab into the clevis on the upper arm piece and secure with an 20mm M5 bolt and nut.

&nbsp;

---

&nbsp;

## Step 7

Insert the sensor into the mounting point on the beam. The sensor should form a smooth slip fit into the holes on the beam. If not, you may need to remove some material from the holes to allow the sensor to fit.

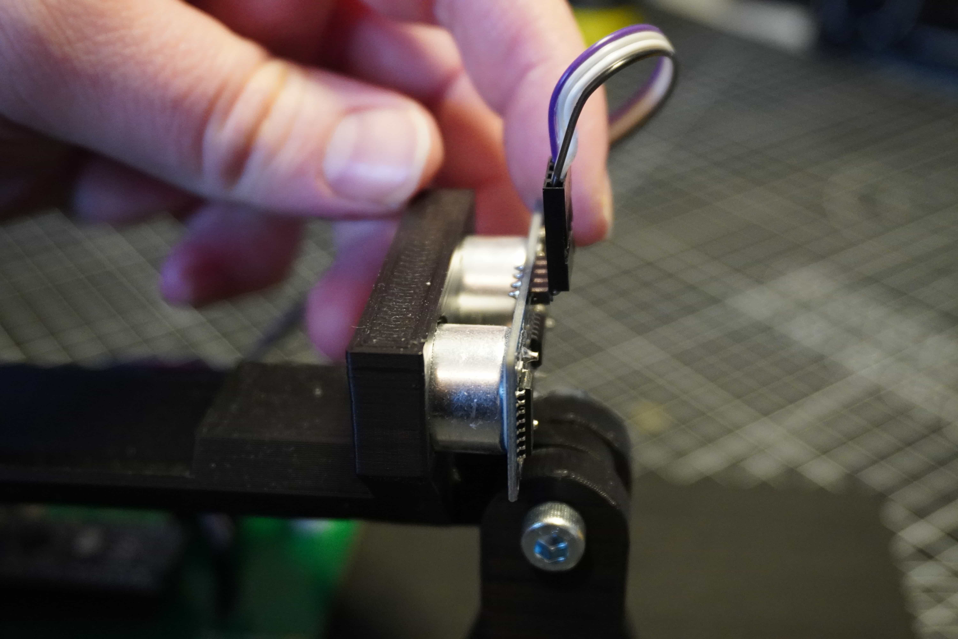
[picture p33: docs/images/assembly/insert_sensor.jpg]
insert_sensor


Pressing the sensor gently, it should push right into the mounting holes to it's final depth as shown. Note, the orientation should be such that the connector it facing upwards to allow clearance for the wires.

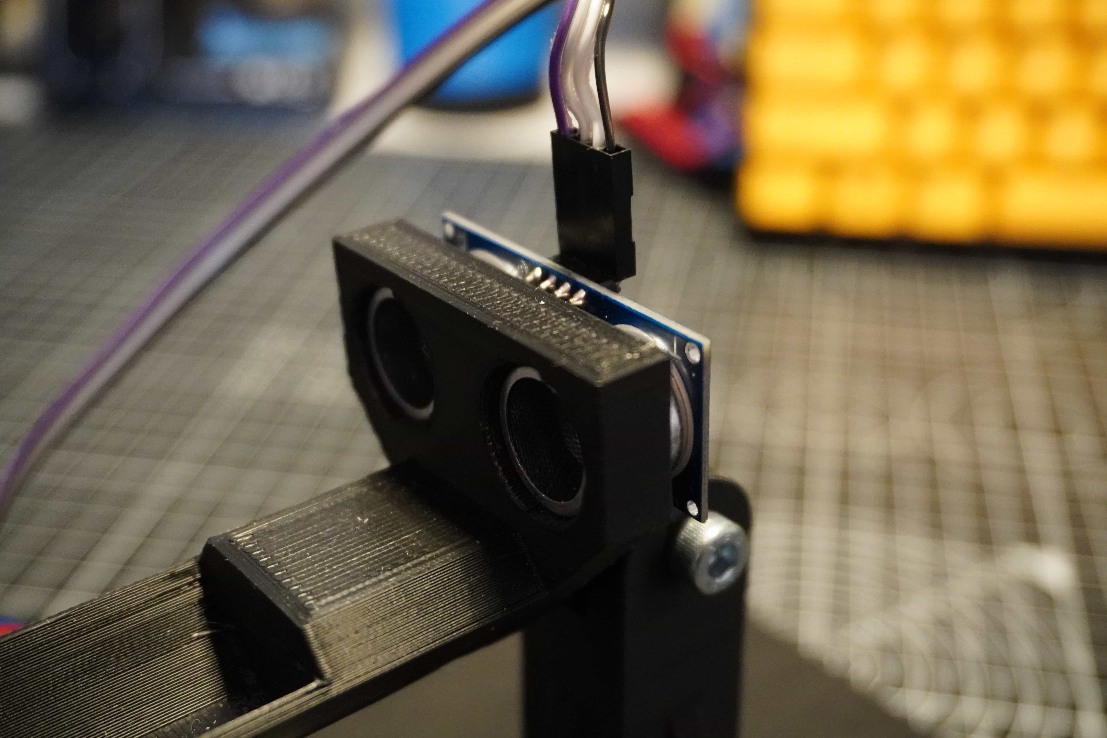
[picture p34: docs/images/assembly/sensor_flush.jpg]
sensor_flush


&nbsp;

---

&nbsp;

## Step 8

With the mechanical assembly now finished, the next steps are to wire everything, upload the code and turn it on! To learn more about these steps, head over to the [Electronics](../electronics) and [Programming](../programming) sections!

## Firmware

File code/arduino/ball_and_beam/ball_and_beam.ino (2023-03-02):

#include <PID_v1.h>
#include <HCSR04.h>
#include <AccelStepper.h>
#include <SimpleKalmanFilter.h>

const int STEP_PIN = 3;
const int DIR_PIN = 2;
const int ECHO_PIN = 6;
const int TRIG_PIN = 5;
const int M0_PIN = 8;
const int M1_PIN = 9;
const int M2_PIN = 10;
const int ENABLE_PIN = 12;
const int STEP_MODE = 5;
const int STEP_MODES[6][4] = {
    {1, 0, 0, 0},  // STEP_MODE = 0
    {2, 1, 0, 0},  // STEP_MODE = 1
    {4, 0, 1, 0},  // STEP_MODE = 2
    {8, 1, 1, 0},  // STEP_MODE = 3
    {16, 0, 0, 1}, // STEP_MODE = 4
    {32, 1, 1, 1}  // STEP_MODE = 5
};

const double MEASUREMENT_ERROR = 0.04;
const double VARIANCE = 1;
const double KP = 27.50;
const double KI = 15.0;
const double KD = 6.0;
const double SET_POINT = 0.0;

double ball_position;
double setPoint, input, output;
double radiansPerStep;

AccelStepper stepper(AccelStepper::DRIVER, STEP_PIN, DIR_PIN);
HCSR04 sensor(TRIG_PIN, ECHO_PIN);
SimpleKalmanFilter filter(MEASUREMENT_ERROR, MEASUREMENT_ERROR, VARIANCE);
PID pid(&input, &output, &setPoint, KP, KI, KD, DIRECT);

void setup()
{
  pinMode(M0_PIN, OUTPUT);
  pinMode(M1_PIN, OUTPUT);
  pinMode(M2_PIN, OUTPUT);
  pinMode(ENABLE_PIN, OUTPUT);
  digitalWrite(ENABLE_PIN, HIGH); // Disable Motor

  double degreesPerStep = 360.00 / (200.00 * STEP_MODES[STEP_MODE][0]); // Assuming a 200 step motor
  radiansPerStep = degreesPerStep * (PI / 180.00);
  stepper.setMaxSpeed(25000);
  stepper.setAcceleration(15000);
  stepper.setMinPulseWidth(5);
  digitalWrite(M0_PIN, STEP_MODES[STEP_MODE][1]);
  digitalWrite(M1_PIN, STEP_MODES[STEP_MODE][2]);
  digitalWrite(M2_PIN, STEP_MODES[STEP_MODE][3]);

  int stepperMax = 25 * STEP_MODES[STEP_MODE][0]; // Allow the motor to move about an 1/8 of a rotation +/-
  int stepperMin = -1 * stepperMax;
  setPoint = SET_POINT;
  pid = PID(&input, &output, &setPoint, KP, KI, KD, DIRECT);
  pid.SetMode(AUTOMATIC);
  pid.SetOutputLimits(stepperMin, stepperMax);

  for (int i = 0; i < 10; i++) // Delay for 2 seconds reading sensor to allow initial values to settle
  {
    readSensor();
    delay(200);
  }
  digitalWrite(ENABLE_PIN, LOW); // Enable Motor
}

void readSensor()
{
  double reading = sensor.dist();
  if (reading > 2.0 && reading < 25.00)
  {
    ball_position = filter.updateEstimate(reading);
  }
}

void move()
{
  stepper.runToNewPosition(-output);
}

void loop()
{
  readSensor();
  double h = 13.5 - ball_position;
  double a = stepper.currentPosition() * radiansPerStep;
  input = h * cos(a);
  pid.Compute();
  move();
}

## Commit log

2023-01-25 Stepper refactor
2023-01-25 Stepper tweaks
2023-01-27 v2 meshes and gcode
    [beam.stl, fulcrum.stl, lower_linkage.stl, motor_mount.stl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]
2023-02-10 v1 board design
    [copper_bottom.gbr, copper_top.gbr, drill_1_16.xln, gerber_job.gbrjob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]
2023-02-21 V1.2 electronics
    [copper_bottom.gbr, copper_top.gbr, drill_1_16.xln, gerber_job.gbrjob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]
2023-03-01 v1.3 electronics
    [copper_bottom.gbr, copper_top.gbr, drill_1_16.xln, gerber_job.gbrjob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]
2023-03-02 code tweaks for v1.3 board and about docs
2023-03-30 Added assembly instructions
2023-03-31 Arduino overview
2023-04-03 stepper motors
